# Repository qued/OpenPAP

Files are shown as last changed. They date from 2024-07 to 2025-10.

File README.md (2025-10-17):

# OpenPAP

A fork of OpenPAP (original [here](https://github.com/keredson/openpap)), an open hardware, open source CPAP / BiPAP solution than can be build for about **$120**.



## Changes from original project
I wanted to make this machine more end-user friendly. To that end, I've utilized a rotary encoder interface to allow the user to configure the machine via a menu system. Currently the menu system supports the following:
* Starting/stopping the therapy cycle (therapy cycle now shows a graph)
* Testing the motor with manual throttle control
* Testing the pressure sensor
* Calibrating the ESC
* Auto tuning the PID parameters system using IMC

I have removed the OTA firmware updates / PID parameter changes for the time being.

## Disclaimer

**WARNING: This project is not approved for medical use.**

This project is provided **as-is**, **without any guarantees** or **warranties of any kind**, express or implied. It is an **experimental, educational, and non-commercial** open-source project intended to explore the design and functionality of CPAP systems.

By using, modifying, or building this project, you acknowledge and agree to the following:

- This project is **not certified** by any regulatory authority (e.g. FDA, CE, ISO).
- It is **not intended to diagnose, treat, cure, or prevent any disease**.
- It **must not be used as a substitute** for a commercially approved CPAP or BiPAP device.
- **Use at your own risk**. The creators and contributors are **not responsible for any harm, injury, or loss** resulting from the use or misuse of this hardware, firmware, or software.
- This device has **not undergone clinical testing** or safety validation.
- No support or liability is implied or offered for any applications of this project in **real-world medical or therapeutic contexts**.

If you are in need of CPAP therapy or respiratory assistance, please consult a qualified medical professional and use approved commercial devices.

## Current Status

This is a WIP, although from my testing, the firmware is in a working state.

## Hardware
- Resmed motor ([example](https://www.amazon.com/gp/product/B0CHYMMM8G))
- 5A 12v to 24v power supply (higher voltages support higher pressures - [example 12v](https://www.amazon.com/gp/product/B08C594VNP) / [example 24v](https://www.amazon.com/ALITOVE-100-240V-Adapter-Converter-5-5x2-1mm/dp/B01GC6VS8I))
- 4S to 6S ESC (brushless motor driver, depending on voltage - [example](https://www.amazon.com/RC-Brushless-Electric-Controller-bullet/dp/B071GRSFBD))
- ESP32 microcontroller ([example](https://www.amazon.com/ESP-WROOM-32-Development-Microcontroller-Integrated-Compatible/dp/B08D5ZD528))
- Air pressure sensor ([example](https://www.amazon.com/gp/product/B09V5BDFF6))
- KY 040 Rotary encoder ([example](https://www.amazon.com/JTAREA-KY-040-Encoder-Encoders-Modules/dp/B0D2TTG858))
- SSD1306 OLED 128x64 Display ([example](https://www.amazon.com/Hosyond-Display-Self-Luminous-Compatible-Raspberry/dp/B09T6SJBV5))
- XT60 Female Bullet Connector to DC5.5X 2.1mm Female Adapter ([example](https://www.amazon.com/cablecc-5-5x2-1mm-Quadcopter-Multicopter-Aeromodelling/dp/B0DLT9P7JK))
- (Optional, for testing) Breadboard
- (Optional, for testing) Jumper wires

## Build Guide

### Wiring

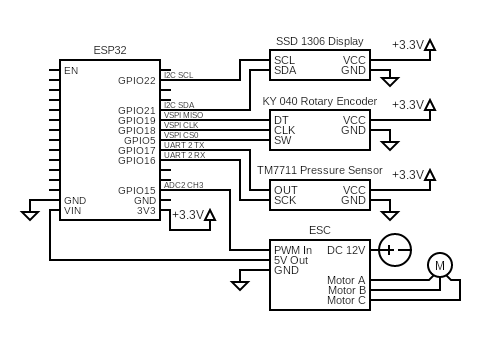
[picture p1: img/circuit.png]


1. Flash firmware onto ESP32. The structure of this project is best suited for PlatformIO, but you can move all files from subfolders of `lib/` and the `.ino` file from `src/` to a folder called `openpap/`, and Arduino IDE should recognize that as a valid project.

2. It's recommended that you wire everything up on a breadboard to test the components. See above diagram for wiring. Unplug the USB cable from the ESP32, and wire up the rest of the components, but don't connect the ESC to the power supply. **The ESP32 should not be connected to USB while the hot wire from the ESC is connected to Vin of the ESP32**.

#### Wiring notes:
- **ESP32 Board:** This guide uses a **30-pin ESP32 DevKit**. If you're using a different variant, you can keep the same GPIO numbers, but be sure to consult a pinout diagram to locate the correct physical pins on your board.
- **Pin Flexibility:** You *can* use different GPIO pins than those listed, but you’ll need to update the `.ino` file before flashing the firmware. Not all GPIOs are suitable for I/O — check your ESP32 documentation first.
- **Powering the Device:** As the diagram shows, the ESC is powered by **12V DC from the power supply**. The ESC powers the motor. The ESC has a BEC connector that contains a **5V+ output line** that powers the ESP32 **through the `VIN` pin**. The ESP32 powers all other components via its **3.3V+ output pin**.
- ⚠️ **Power Warning:** You will need to connect the ESP to USB while flashing firmware and testing. **Do not connect the ESC's 5V wire to the ESP32's `VIN` pin while the ESP32 is also connected to USB.** This can cause voltage backfeeding, which risks damaging your computer, USB port, or the ESP32.
- **Powering the Components while Testing:** While testing, the ESP32 can be powered from USB while the ESC and motor are powered from the power supply, by *disconnecting* the ESC from the `VIN` pin, connecting the ESP32 to USB, and connecting the power supply to the ESC. The system will function in this configuration, while allowing the ESP32 to receive firmware updates and/or send messages to the serial monitor.
- **Motor Wiring Order:** The three motor wires can be connected in **any order**. If the motor spins the wrong direction, simply **swap any two wires**.
- **Motor Connector Tip:** The recommended ESC uses **female 3.5mm bullet connectors**, while the ResMed blower uses a **Molex Mini-Fit Jr.** connector. Instead of using an adapter, I cut off the Molex and soldered on **3 male bullet connectors** to match the ESC.
- **ESC Receiver Wires:** For the recommended ESC, the 3 wires that attach to the ESP32 are color-coded instead of labeled. Black is ground, red is +5V DC, and white is the signal wire for PWM control.
- **Static Electricity Warning:** Exercise caution when handling electronic components. A static discharge from your skin can damage sensitive electronics. Avoid touching the circuitry or embedded components by holding components by the edges of their breakout boards.

### Setup

Once the firmware is flashed and the components are wired up, it's time to set up the system and begin testing.

1. Power on the system, and wait for the menu to appear.
1. Move the rotary encoder, and ensure that you are able to navigate the menu.
1. Select "Settings" and press the rotary encoder button.
1. Select "Calibrations"
1. Select "Cal. Speed Control" and follow the instructions.
1. After finishing the ESC calibration, select "Settings" again from the main menu
1. Select "Test Components"
1. Select "Test Motor" 
1. Turn the dial to the right to increase the motor speed. Ensure the motor is responding to the various speeds.
1. Exit the motor test mode
1. Select "Test Press. Sensor"
1. Ensure the pressure sensor is responding to stimuli. Blow lightly on the pressure sensor nozzle and see if the reading jumps.
1. The "Calibrate CPAP" cycle should be run only after mounting the motor in the shell with the pressure sensor and hose attached.

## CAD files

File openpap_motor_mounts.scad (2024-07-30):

use <openpap.scad>;
motor_mounts();

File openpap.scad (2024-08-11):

T = 3;
motor_opening_d = 64;
motor_offset = 6;
corner_r = 8;
cube_w = motor_opening_d + 2*T - 2*corner_r;
w = cube_w + 2*corner_r;
electronics_w = 32;
cube_l = cube_w+motor_offset+electronics_w+T;
l = cube_l + 2*corner_r;
button_d = 12.5;


module motor() {
  d1 = 59;
  d2 = 53;
  out_d = 22;
  h2 = 10.5;
  h1 = 44;
  out_h = 4.5;
  cylinder(h1, d1/2, d1/2);
  translate([0,0,h1]) cylinder(h2, d2/2, d2/2);
  translate([0,0,h1+h2]) cylinder(out_h, out_d/2, out_d/2);
}

module motor_mounts() {
  for (i=[0:2]) translate([i*7-10,15,0]) 
  difference() {
    cube([6, 19, 6]);
    translate([2,0,3]) cube([2, 19, 3]);
  }
  difference() {
    cylinder(5, 22/2+T, 22/2+1);
    cylinder(5, 22/2, 22/2);
  }
}

module display() {
  translate([-28/2,-14/2-5,-3]) {
    difference() {
      cube([28,28,3]);
      for (i=[2, 28-2]) for (j=[2, 28-2]) translate([i,j,1]) cylinder(2,.1,1, $fn=20);
    }
    translate([1,5,0]) cube([26,14,6]);
  }
}

module lid_cutout() {
      translate([corner_r, corner_r, 0]) minkowski() {
        cube([cube_w,cube_l,100]);
        cylinder(r=corner_r-2,h=T);
      }
}

module shell() {
  motor_top_inset = 16;
  motor_opening_h = 45+4 + motor_top_inset;
  h = motor_opening_h + T;
  filter_l = 54;
  filter_w = 35;
  filter_t = 6;

  translate([0,0,-h]) difference() {
    union() {
      translate([corner_r, corner_r, 0]) minkowski() {
        cube([cube_w,cube_l,h]);
        cylinder(r=corner_r,h=T);
      }
    }
    translate([corner_r, 2*T+motor_opening_d+motor_offset+(corner_r-T), T]) minkowski() {
      cube([cube_w,cube_l-motor_opening_d-motor_offset-T,h-T-1]);
      cylinder(r=corner_r-T,h=1);
    }
    translate([motor_opening_d/2+T,motor_offset+motor_opening_d/2+T,T]) cylinder(h=100, r=motor_opening_d/2);
    
    translate([0,0,h]) lid_cutout();
        
    // motor notches
    for(i=[0,120,240]) translate([(motor_opening_d+2*T)/2,motor_offset+(motor_opening_d+2*T)/2,h]) 
    rotate([0,0,i-30]) translate([(motor_opening_d)/2,0,0]) cube([2,6,(15+4*2+motor_top_inset)*2], center=true);
    
    // filter
    hole_r = 2.5;
    translate([(motor_opening_d+2*T-filter_l)/2,2,0]) cube([filter_l, filter_t, filter_w]);
    //translate([(motor_opening_d+2*T-hole_r*2)/2,0,0]) cube([hole_r*2, filter_t, 7]);
    for (i=[-3:3]) for (j=[0,1,2])
    translate([i*7.5+(motor_opening_d+2*T)/2,0,7+j*12]) rotate([-90,0,0]) cylinder(20, r=hole_r, $fn=20);
    for (i=[-3:2]) for (j=[0,1])
    translate([(i+.5)*7.5+(motor_opening_d+2*T)/2,0,13+j*12]) rotate([-90,0,0]) cylinder(20, r=hole_r, $fn=20);
    
    // wires
    for (i=[1:3]) translate([i*10+T+3,motor_opening_d-15,T+3]) rotate([-90,0,0]) cylinder(40, r=4);
      
    translate([(motor_opening_d+2*T)/2,cube_l+corner_r*2-1,(h+T)/2]) mirror([0,1,0]) rotate([90,90,0]) display();

    // button
    translate([(motor_opening_d+2*T)/2,cube_l+corner_r*2-18,(h+T)/2]) rotate([0,90,0]) cylinder(h=100, r=button_d/2);

    // screw holes
    for (i=[0,1]) for (j=[0,1]) translate([corner_r +i*cube_w,corner_r+j*(cube_w+3*T),h-17]) cylinder(20,r=1, $fn=10);
        
    // power adapter
    translate([T+15/2,l-electronics_w/2-T,-T]) cylinder(T*2, r=11.5/2);
    
  }
}

module lid() {
  air_hole_h = 3;
  intersection() {
      lid_cutout();
      difference() {
        union() {
          translate([corner_r, corner_r, 0]) minkowski() {
            cube([cube_w,cube_l,T-1]);
            cylinder(r=corner_r,h=1);
          }
          translate([corner_r+cube_w/2,motor_offset+corner_r+cube_w/2,0]) {
            cylinder(air_hole_h+T, 22/2+2*T, 22/2+1+T);
            cylinder(air_hole_h+T+20, 25/2, 23/2);
            pressure_tube_l = motor_opening_d/2+T+electronics_w/2;
            translate([0,0,air_hole_h]) rotate([-90,0,0]) cylinder(pressure_tube_l, r=3, $fn=20);
          }
        }
        // screw holes
        for (i=[0,1]) for (j=[0,1]) translate([corner_r +i*cube_w,corner_r+j*(cube_w+3*T),0]) cylinder(20,r=1, $fn=10);

        translate([corner_r+cube_w/2,motor_offset+corner_r+cube_w/2,0]) {
          cylinder(100, r=19/2);
          translate([0,0,air_hole_h]) rotate([-90,0,0]) cylinder(cube_w-6, r=1.6, $fn=20);
          translate([0,cube_w-7,0]) cylinder(air_hole_h, r=1.6, $fn=20);
        }

      }
  }
}

//motor();
motor_mounts();
//shell();
//translate([0,0,2*T]) lid();
//display();

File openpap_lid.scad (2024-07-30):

use <openpap.scad>;
lid();

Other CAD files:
openpap_shell.scad

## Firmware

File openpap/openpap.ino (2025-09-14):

#include <Arduino.h>
#include <Preferences.h>
#include "ESCController.h"
#include "KY_040.h"
#include "DisplayManager.h"
#include "TM7711PressureSensor.h"
#include "MenuSystem.h"
#include "debouncedbutton.h"
#include "PID.h"
#include "OpenPAPMenu.h"

// --- Pin Definitions ---
// ESC Motor Controller
#define ESC_PIN 15
// Rotary Encoder
#define SW_PIN 5
#define CLK_PIN 18
#define DT_PIN 19
// Display
#define SDA_PIN 21
#define SCL_PIN 22
#define SCREEN_WIDTH 128
#define SCREEN_HEIGHT 64
// Pressure Sensor
#define SCK_PIN 16
#define OUT_PIN 17

#define CALIBRATION_FACTOR 28426.0

// --- Globals ---
ESCController esc(ESC_PIN);
RotaryEncoder encoder(CLK_PIN, DT_PIN);
DisplayManager display(SCREEN_WIDTH, SCREEN_HEIGHT, SDA_PIN, SCL_PIN);
TM7711PressureSensor pressure_sensor(SCK_PIN, OUT_PIN);
DebouncedButton button(SW_PIN);

MenuSystem menu(&display, &mainMenu);

Preferences preferences;

void setup() {

  preferences.begin("OpenPAP", false);
  bool escCalibrate = preferences.getBool("esc_cal", false);
  esc.begin();
  if (escCalibrate) {
    // Calibration mode is triggered when the ESC is powered on and immediately receives a full throttle signal
    esc.setThrottle(1.0);
    Serial.begin(115200);
    Serial.println("ESC Calibration mode detected!");
    encoder.begin();
    display.begin();
    preferences.remove("esc_cal");  // Make sure the next boot is in normal mode
    preferences.end();
    menu.setActiveView(escCalibrationMaxLoop, escCalibrationMaxDraw);
  } else {
    float Kp = preferences.getFloat("Kp", 1.0);
    float Ki = preferences.getFloat("Ki", 0.0);
    float Kd = preferences.getFloat("Kd", 0.0);
    preferences.end();
    Serial.begin(115200);
    esc.arm();
    encoder.begin();
    display.begin();
    display.showStartup("Starting...");
  }

  pressure_sensor.begin();
  pressure_sensor.setRate(RATE40Hz);
  pressure_sensor.tare();
  pressure_sensor.setCalibrationFactor(CALIBRATION_FACTOR);

  menu.draw();
}

void loop() {
  button.update();

  menu.update(encoder.getDelta(), button.wasPressed());
}

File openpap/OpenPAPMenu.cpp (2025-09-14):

#include "OpenPAPMenu.h"

// --- Submenus ---
MenuList calibrationsMenu = MenuList::withItems({
  MenuItem("Calibrate Motor", calibrateESC),
  MenuItem("Calibrate CPAP", calibratePID),
  MenuItem("Back", goBack)
});

MenuList testComponentsMenu = MenuList::withItems({
  MenuItem("Test Motor", testMotor),
  MenuItem("Test Press. Sensor", testPressure),
  MenuItem("Back", goBack)
});

MenuList settingsMenu = MenuList::withItems({
  MenuItem("Calibrations", nullptr, &calibrationsMenu),
  MenuItem("Test Components", nullptr, &testComponentsMenu),
  MenuItem("Back", goBack)
});

MenuList mainMenu = MenuList::withItems({
  MenuItem("Start Therapy", beginTherapy),
  MenuItem("Settings", nullptr, &settingsMenu),
  MenuItem("About", showAbout)
});

// --- Actions ---
void notImplemented() {
  Serial.println("Not implemented");
}

void beginTherapy() {
  Serial.println("Entering therapy loop...");
  menu.setActiveView(therapyLoop, therapyDraw);
}

void testMotor() {
  Serial.println("Entering motor test...");
  menu.setActiveView(motorTestLoop, motorTestDraw);
}

void testPressure() {
  Serial.println("Entering pressure test...");
  menu.setActiveView(pressureTestLoop, pressureTestDraw);
}

void calibrateESC() {
  Serial.println("Entering ESC calibration mode...");
  preferences.begin("OpenPAP", false);
  preferences.putBool("esc_cal", true);
  Serial.print("Wrote to preferences: ");
  Serial.println(preferences.getBool("esc_cal", false));
  preferences.end();
  menu.setActiveView(escCalibrationPreLoop, escCalibrationPreDraw);
}

void calibratePID() {
  Serial.println("Entering PID calibration...");
  menu.setActiveView(pidCalibrationLoop, pidCalibrationDraw);
}

void showAbout() {
  Serial.println("OpenPAP v1.0");
  // Display info on screen
}

void goBack() {
  menu.goBack();  // Built-in function to navigate back in menu
}

// --- Active Views ---

// --- Therapy ---

void therapyLoop(int delta, bool buttonPressed) {
  static enum { INIT, RAMP_UP, THERAPY, RAMP_DOWN, DONE} state = INIT;
  static float input = 0.0;
  static float output = 0.0;
  static float setpoint = 12.0;
  static const float out_min = 0.0;
  static const float out_max = 1.0;
  static unsigned long last_read_time = 0;
  static unsigned long current_read_time = 0;
  static float dt = 0.001f;
  static float K = 0.0f;
  static float theta = 0.0f;
  static float tau = 0.0f;
  static const float FAULT_TOLERANCE_FACTOR = 5.0f;
  static float FAULT_THRESHOLD = 0.0f;
  static PID pid(&input, &output, setpoint, 1.0, 0.0, 0.0, out_min, out_max);

  switch (state) {
    case INIT: {
      preferences.begin("OpenPAP", true);
      float Kp = preferences.getFloat("Kp", 1.0);
      float Ki = preferences.getFloat("Ki", 0.0);
      float Kd = preferences.getFloat("Kd", 0.0);
      K = preferences.getFloat("K", 1.0);
      tau = preferences.getFloat("tau", 1.0);
      theta = preferences.getFloat("theta", 1.0);
      preferences.end();
      pid.setTunings(Kp, Ki, Kd);
      pid.reset();
      FAULT_THRESHOLD = FAULT_TOLERANCE_FACTOR * setpoint * tau;
      input = pressure_sensor.getPressure();
      last_read_time = pressure_sensor.lastReadTime();
      state = RAMP_UP;
      break;
    }

    case RAMP_UP:
      // TODO: Add ramp up phase.
      state = THERAPY;
      break;

    case THERAPY:
      input = pressure_sensor.getPressure();
      current_read_time = pressure_sensor.lastReadTime();
      dt = (current_read_time - last_read_time) / 1000.0f;
      pid.compute(dt); // output should update as a side effect.
      esc.setThrottle(output);
      last_read_time = current_read_time;
      if (fabs(pid.error_sum) > FAULT_THRESHOLD ) {
        // Fault -- System is not responding
        Serial.println("Fault tolerance exceeded, exiting therapy loop.");
        state = RAMP_DOWN;
      }
      if (buttonPressed) {
        state = RAMP_DOWN;
      }
      break;

    case RAMP_DOWN:
      esc.stop(); // TODO: Add ramp down phase.
      state = DONE;
      break;

    case DONE:
      if (buttonPressed) {
        state = INIT;
        menu.exitActiveView();
      }
      break;
  }
}

void therapyDraw() {
  display.printLines(
    "Throttle: " + String((int)(100*esc.getThrottle())) + "%",
    "Pressure: " + String(pressure_sensor.lastReading) + " cmH2O"
  );
}

// --- Motor Test ---

void motorTestLoop(int delta, bool buttonPressed) {
  if (delta != 0) {
    double currThrottle = esc.getThrottle();
    double newThrottle = currThrottle + delta * .05;

    // Update ESC here
    esc.setThrottle(newThrottle);
  }

  if (buttonPressed) {
    esc.stop();
    menu.exitActiveView();  // Return to menu
  }
}

void motorTestDraw() {
  display.printLines(
    "Motor Test",
    "Throttle: " + String((int)(100*esc.getThrottle())) + "%",
    " ",
    "Rotate to adjust",
    "Press to exit"
  );
}

// --- Pressure Sensor Test ---
void pressureTestLoop(int delta, bool buttonPressed) {
  if (buttonPressed) {
    menu.exitActiveView();  // Return to menu
  }
}

void pressureTestDraw() {
  display.printLines(
    "Pressure Sensor Test",
    "--------------------",
    "Raw: " + String(pressure_sensor.getRawPressure()),
    "Pressure: " + String(pressure_sensor.getPressure()) + " cmH2O",
    "Tare Value: " + String(pressure_sensor.getZeroValue()),
    "Cal Factor: " + String((long)pressure_sensor.getCalibrationFactor()),
    "Press to exit"
  );
}

// --- ESC Calibration ---
void escCalibrationPreLoop(int delta, bool buttonPressed) {
  if (buttonPressed) { // User cancels calibration
    preferences.begin("OpenPAP", false);
    preferences.remove("esc_cal");
    preferences.end();
    menu.exitActiveView();  // Return to menu
  }
}

void escCalibrationPreDraw() {
  display.printLines(
    "Motor Calibration",
    "-----------------",
    "Power off and on now,",
    "or press button to ",
    "cancel..."
  );
}

void escCalibrationMaxLoop(int delta, bool buttonPressed) {
  if (buttonPressed) {
    esc.stop();
    Serial.println("Leaving ESC calibration mode...");
    menu.setActiveView(escCalibrationMinLoop, escCalibrationMinDraw); // Go to next screen
  }
}

void escCalibrationMaxDraw() {
  display.printLines(
    "Motor Calibration",
    "-----------------",
    "Motor should emit 4 ",
    "beeps.",
    " ",
    "Press button before ",
    "they end."
  );
}

void escCalibrationMinLoop(int delta, bool buttonPressed) {
  if (buttonPressed) {
    menu.setActiveView(escCalibrationEndLoop, escCalibrationEndDraw);
  }
}

void escCalibrationMinDraw() {
  display.printLines(
    "Motor Calibration",
    "-----------------",
    "Two short beeps",
    "followed by two long",
    "beeps, indicates",
    "success.",
    "Press to continue..."
  );
}

void escCalibrationEndLoop(int delta, bool buttonPressed) {}

void escCalibrationEndDraw() {
  display.printLines(
    "Motor Calibration",
    "-----------------",
    "Calibration complete!"
    " ",
    "Power off now.",
    "(If calibration was",
    "unsuccessful, retry)"
  );
}

// --- PID Calibration ---

void pidCalibrationLoop(int delta, bool buttonPressed) {
  static enum { INIT, APPLY_STEP, LOGGING, ANALYSIS, DONE } state = INIT;
  static uint32_t startTime = 0;
  static const unsigned int MAX_SAMPLES = 160;
  static float pressureLog[MAX_SAMPLES];
  static uint32_t timeLog[MAX_SAMPLES];
  static size_t sampleCount = 0;

  switch (state) {
    case INIT:
      startTime = millis();
      sampleCount = 0;
      state = APPLY_STEP;
      break;

    case APPLY_STEP:
      esc.setThrottle(1.0);
      state = LOGGING;
      break;

    case LOGGING:
      if (sampleCount < MAX_SAMPLES) {
        pressureLog[sampleCount] = pressure_sensor.getPressure();
        timeLog[sampleCount] = millis() - startTime;
        sampleCount++;
      } else {
        esc.stop();
        state = ANALYSIS;
      }
      break;

    case ANALYSIS: {
      const size_t avgWindow = 10;
      const size_t confirmWindow = 3;

      // --- Step 1: Smoothed Initial and Final Pressure ---
      float sumStart = 0.0f, sumEnd = 0.0f;
      for (size_t i = 0; i < avgWindow; i++) {
        sumStart += pressureLog[i];
        sumEnd   += pressureLog[MAX_SAMPLES - 1 - i];
      }
      float P0 = sumStart / avgWindow;
      float Pfinal = sumEnd / avgWindow;
      float deltaP = Pfinal - P0;

      if (fabs(deltaP) < 0.01f) {
        Serial.println("Calibration failed: no significant pressure change");
        state = DONE;
        break;
      }

      // --- Step 2: Calculate Process Gain K ---
      float deltaInput = 0.5f; // Motor throttle step
      float K = deltaP / deltaInput;

      // --- Step 3: Find Dead Time (θ) ---
      float P5 = P0 + 0.05f * deltaP;
      size_t indexTheta = 0;
      for (size_t i = 0; i < sampleCount - confirmWindow; i++) {
        bool stable = true;
        for (size_t j = 0; j < confirmWindow; j++) {
          if (pressureLog[i + j] < P5) {
            stable = false;
            break;
          }
        }
        if (stable) {
          indexTheta = i;
          break;
        }
      }
      float theta = timeLog[indexTheta] / 1000.0f;

      // --- Step 4: Find Time Constant (τ) ---
      float P63 = P0 + 0.63f * deltaP;
      size_t indexTau = indexTheta;
      for (size_t i = indexTheta; i < sampleCount - confirmWindow; i++) {
        bool stable = true;
        for (size_t j = 0; j < confirmWindow; j++) {
          if (pressureLog[i + j] < P63) {
            stable = false;
            break;
          }
        }
        if (stable) {
          indexTau = i;
          break;
        }
      }
      float timeAt63 = timeLog[indexTau] / 1000.0f;
      float tau = timeAt63 - theta;

      if (tau <= 0 || theta <= 0 || K == 0) {
        Serial.println("Calibration failed: invalid tau or theta");
        state = DONE;
        break;
      }

      // --- Step 5: Apply Cohen-Coon PID Tuning ---
      float R = theta / tau;
      const float lambda = theta;

      // float Kp = (1.35f + R / 20.0f) * (tau / (K * theta));
      // float Ti = theta * (32.0f + 6.0f * R) / (13.0f + 8.0f * R); // sec
      // float Td = theta * (4.0f * R) / (11.0f + 2.0f * R);         // sec

      // float Ki = Kp / Ti;
      // float Kd = Kp * Td;
      float Kp = tau / (K * (lambda + theta));
      float Ki = Kp / tau;
      float Kd = Kp * theta / 2;
      // --- Step 6: Store Results ---
      preferences.begin("OpenPAP", false);
      preferences.putFloat("Kp", Kp);
      preferences.putFloat("Ki", Ki);
      preferences.putFloat("Kd", Kd);
      preferences.putFloat("K", K);
      preferences.putFloat("tau", tau);
      preferences.putFloat("theta", theta);
      preferences.end();

      Serial.println("Calibration complete:");
      Serial.printf("Kp = %.3f, Ki = %.3f, Kd = %.3f\n", Kp, Ki, Kd);
      Serial.printf("K = %.3f, τ = %.3f, θ = %.3f\n", K, tau, theta);

      state = DONE;
      break;
    }

    case DONE:
      // Wait for user to press button to return to menu
      if (buttonPressed) {
        state = INIT;
        menu.exitActiveView();
      }
      break;
  }
}

// void pidCalibrationLoop(int delta, bool buttonPressed) {
//   static enum { INIT, RUNNING, ANALYSIS, DONE } state = INIT;

//   static const float setpoint = 12.0f;          // Target pressure for autotune
//   static const float highThrottle = 1.0f;       // Relay ON throttle
//   static const float lowThrottle = 0.0f;        // Relay OFF throttle
//   static const size_t MAX_SAMPLES = 800;        // Max samples to collect
//   static const unsigned int minOscillations = 5; // Minimum oscillations before analysis

//   static float pressureLog[MAX_SAMPLES];
//   static uint32_t timeLog[MAX_SAMPLES];
//   static size_t sampleCount = 0;

//   static float lastError = 0.0f;
//   static unsigned long lastZeroCrossTime = 0;
//   static unsigned int zeroCrossCount = 0;
//   static unsigned long startTime = 0;

//   static float peakPressureMax = -1e6;
//   static float peakPressureMin = 1e6;
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

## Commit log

2024-07-31 arduino code starting point
2024-07-31 moved pid loop into a thread
2024-08-02 mount for power jack and a bunch of other tweaks
    [openpap.scad]
2024-08-03 set display rotation for the new case adjusted pid tuning
2024-08-03 motor mounts were off by 4mm
    [openpap.scad]
2024-08-11 misc updates / corrections from first print
    [openpap.scad]
2024-08-31 added Kp, Ki, Kd to settings changed internal pressure representation from mmH2O to cmH20
2025-09-15 Improve PID calibration inline comments
2025-09-15 Rewrite ESC calibration to use shared state in one class
2025-09-17 Fix motor test weird throttle values
2026-01-16 Drop the one function that makes this dependent on arduino.h
2026-02-08 Add system response calibration
2026-02-08 add 0 throttle pressure measurement
2026-02-14 Switch to HAL for ESC and pressure sensor
2026-02-18 Update PID calibration
2026-02-28 Turn off motor when leaving all components test
